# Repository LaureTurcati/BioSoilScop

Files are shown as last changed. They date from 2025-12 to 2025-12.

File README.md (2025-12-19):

# BioSoilScop
The VerY cool Cam Trap for soil ORganisms (VYCTOR)

This camera trap was designed to study ground fauna without disturbing or killing it.

VYCTOR consists of a waterproof sensor measuring approximately 25x25cm with removable and interchangeable 10cm feet. It is capable of taking images day and night thanks to a brightness detection device that activates a night vision mode with 8 infrared LEDs surrounding the camera. The system is controlled by a Raspberry Pi. The camera films continuously at low resolution (without recording) and an algorithm detects movement by comparing images in pairs (background subtraction + speed calculation + shape detection). When movement is detected, a series of high-definition photos is taken at regular intervals and stored. The device is powered by mains electricity or battery. A computer interface allows the measurement settings to be configured and the characteristics of the installation site to be entered. It has been designed to be easy to use by non-specialists.

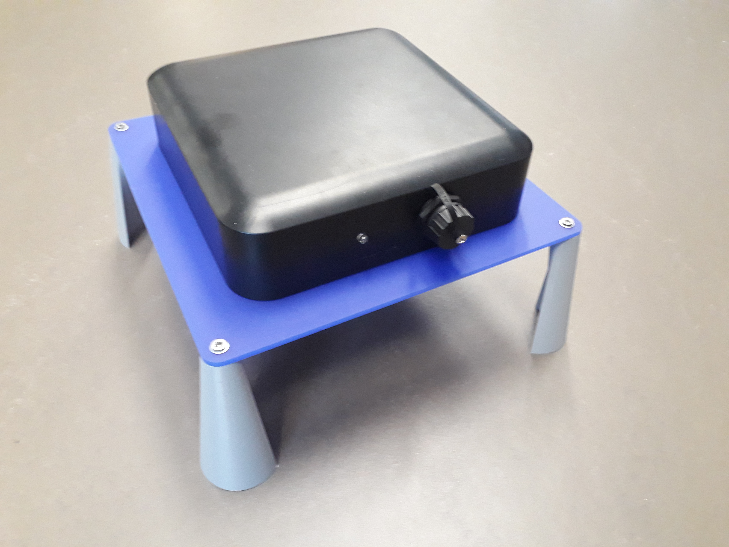
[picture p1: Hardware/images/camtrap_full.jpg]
full

<ins>Picture of the VYCTOR device </ins>  

 ## Examples of pictures taken
Here are some images taken during a laboratory test session.

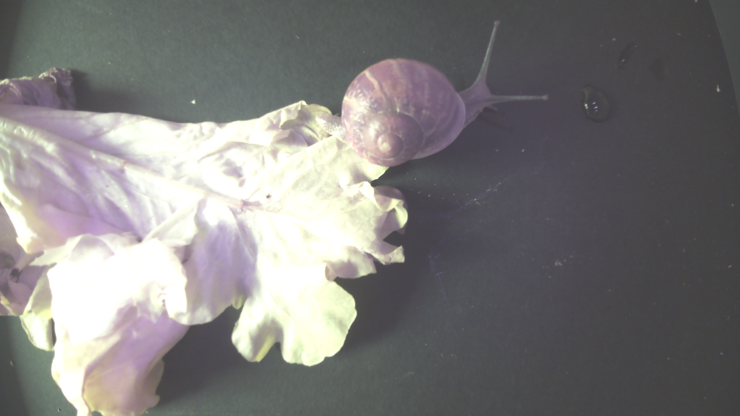
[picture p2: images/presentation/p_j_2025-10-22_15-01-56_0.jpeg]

<ins>Taken picture of a snail after motion detection</ins>

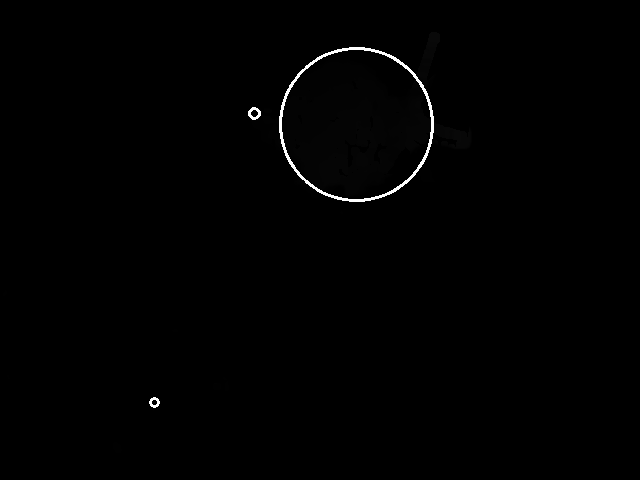
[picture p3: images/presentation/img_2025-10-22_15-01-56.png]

<ins>Motion detection representation</ins>

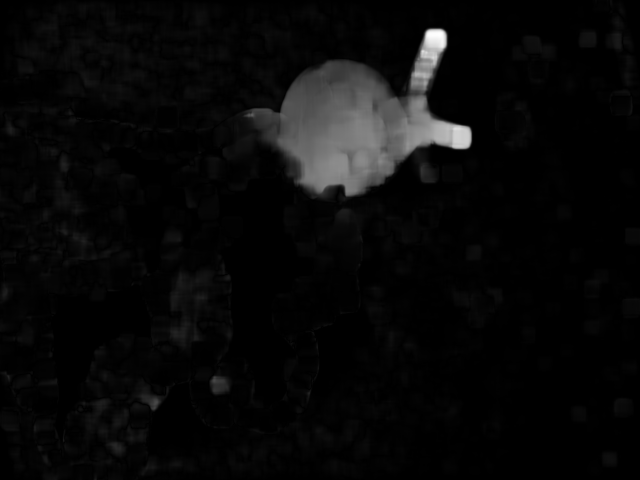
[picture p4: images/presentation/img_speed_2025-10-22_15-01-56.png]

<ins>Speed detection representation</ins>

## Construction
Browse the hardware folder to construct your VYCTOR

## Documentation
Recover the documentation user and developpement in the Folder Software

## Credit
This project was funded by the French national research agency (ANR) BISES ANR-19-CE 32-0012, the OSU OREME and the OSU Ecce Terra

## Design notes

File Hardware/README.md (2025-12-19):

# CamTrap Hardware

Le CamTrap est organisé autour d'un Raspberry Pi.  
Il contient des parties imprimées en 3D et découpé au laser, cependant il est possible de faire sans.

## logiciels utilisés

Les PCBs ont été réalisés avec Kicad 7.0.
Les tracés laser avec Inkscape.

## Liste du Matériel

La liste du matériel se trouve dans le fichier "camtrap_bom.xlsx".

## Schéma de connection

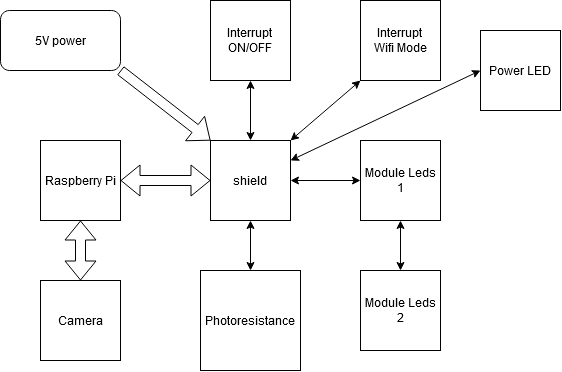
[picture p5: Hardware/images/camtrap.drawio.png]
connections


## Liste des dossiers

Hardware  
├── camtrap/    
├── camtrap_usb_adapteur/  
├── camtrap3d/  
├── images/  
└── camtrap-leds/  

- **`camtrap`** : Contient les fichiers de fabrication de la carte head au dessus du Raspberry.  
- **`camtrap_usb_adapteur`** : Contient les fichiers de fabrication de la petite carte d'adaptation de la prise USB.  
- **`camtrap3d`** : Contient les fichiers d'impression et de découpe.  
- **`images`** : Contient les images pour le readme.  
- **`camtrap-leds`** :  Contient les fichiers de fabrication de la carte qui tient les leds

## Vue globale 

full

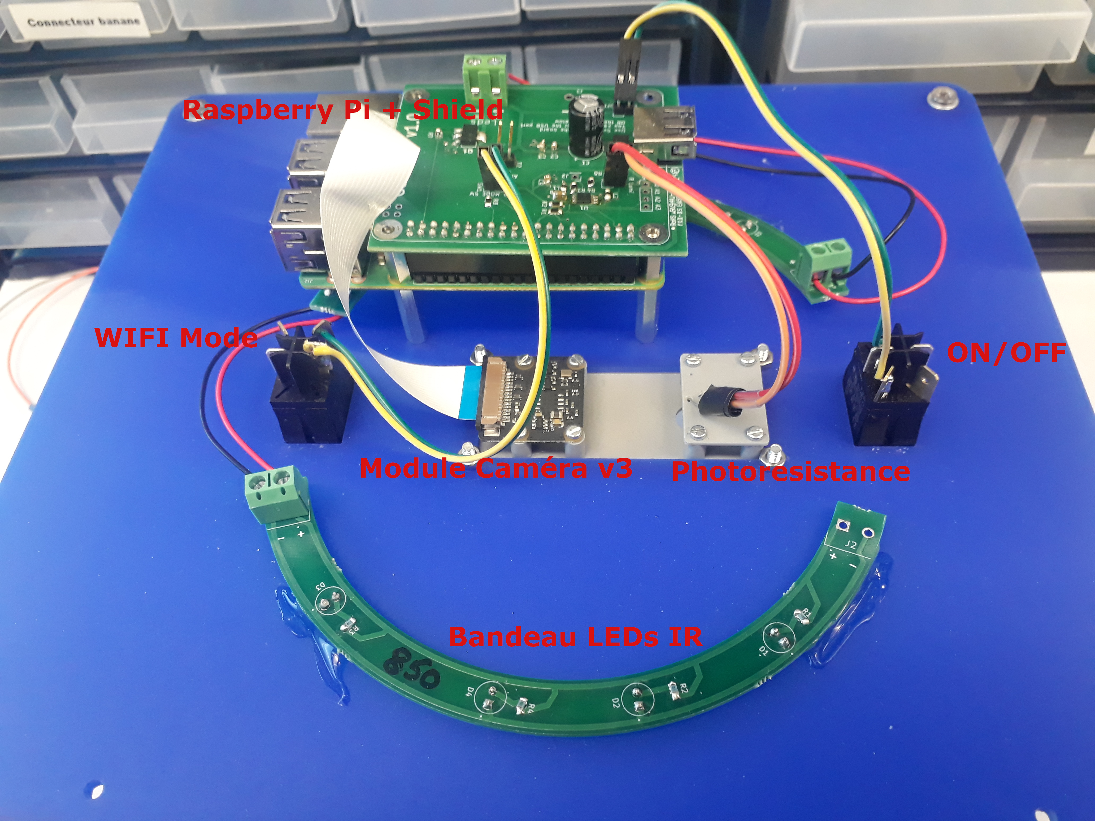
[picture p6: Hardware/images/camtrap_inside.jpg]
inside


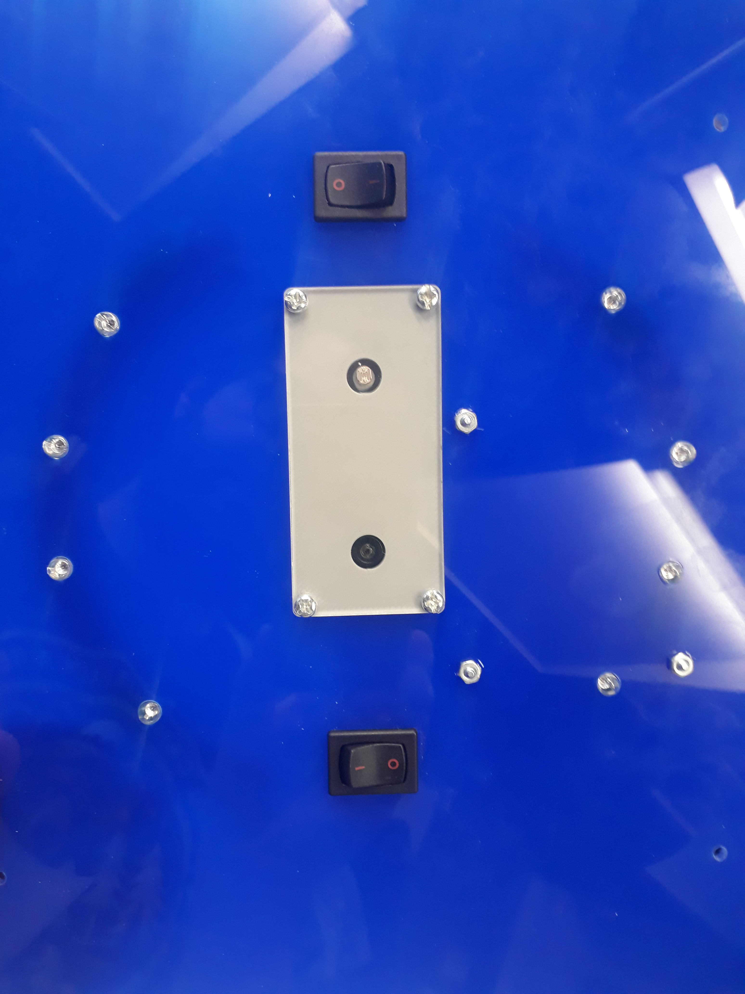
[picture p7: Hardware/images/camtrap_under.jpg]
under


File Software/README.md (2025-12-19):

# CamTrap Software

[Mettre un OS sur le Raspberry pi](./RaspberryPiOS.md)

## Interface

[Documentation développement](./interface/Readme.md)  
[Documentation utilisation](./interface/CamTrap.md)  

## Application

[Documentation](./application/Readme.md)

## Organisation

home/  
├── ADS1115/  
├── app/  
├── interface/  
└── camtrap/  

- **`ADS1115`** : Environnement utile pour l'app
- **`app`** : Application
- **`interface`** : Interface
- **`camtrap`** : Dossier de stockage des config, et des dossiers de sessions.

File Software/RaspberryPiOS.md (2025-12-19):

# Installation d'un OS sur un Raspberry Pi avec Raspberry Pi Imager

Ce guide est un rappel pour installer un OS sur un Raspberry Pi en utilisant **Raspberry Pi Imager** sous Ubuntu.

---

## 1. Installation de Raspberry Pi Imager

### 1.1 Via le Store Ubuntu

1. Ouvrir le **Store Ubuntu**.
2. Rechercher et installer **Raspberry Pi Imager**.

### 1.2 Installation manuelle via fichier .deb

1. Télécharger le fichier `.deb` depuis le site officiel : [Raspberry Pi Imager](https://www.raspberrypi.org/software/).
   - Exemple de fichier : `imager_x.x.x_amd64.deb`
2. Ouvrir un terminal et exécuter les commandes suivantes :

    ```bash
    cd ~/Téléchargements
    sudo apt install ./imager_x.x.x_amd64.deb
    ```

---

## 2. Télécharger et flasher l'OS

### 2.1 Utilisation de Raspberry Pi Imager

1. Ouvrir **Raspberry Pi Imager**.
2. Rechercher et sélectionner l'OS souhaité dans la liste proposée.

### 2.2 Si l'OS n'est pas disponible dans la liste

1. Télécharger l'image `.zip` de l'OS depuis un site officiel.
2. (Optionnel) Vérifier l'intégrité du fichier téléchargé en comparant le **hash SHA256**.

#### Vérification du fichier avec SHA256

- Télécharger également le fichier `.zip.sha256`.
- Calculer le hash du fichier téléchargé :

    ```bash
    sha256sum ./chemin/vers/fichier.zip
    ```

- Comparer le résultat avec le contenu du fichier `.zip.sha256` :

    ```bash
    diff <(sha256sum ./chemin/vers/fichier.zip) fichier.sha256
    ```

Si le hash est correct, vous pouvez continuer.

### 2.3 Flash de l'OS sur la carte SD

1. Insérer la **carte SD** du Raspberry Pi dans le PC.
2. Dans **Raspberry Pi Imager**, choisir **"Use custom"** pour sélectionner l'image téléchargée.
3. Sélectionner la **carte SD** comme destination de l'écriture.
4. Cliquer sur **"Écrire"** pour flasher l'OS.

---

## 3. Préparer le Raspberry Pi

1. Retirer la carte SD du PC et l'insérer dans le Raspberry Pi.
2. Démarrer le Raspberry Pi.

### 3.1 Mettre à jour le Raspberry Pi

1. Mettre à jour la date du système (si nécessaire) :

    ```bash
    sudo date -s 'yyyy-mm-dd hh:mm:ss'
    ```

2. Mettre à jour les paquets du système :

    ```bash
    sudo apt update
    sudo apt upgrade
    ```

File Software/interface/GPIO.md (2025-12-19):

# GPIO

##### Mise en place du bouton 

| Couleur du fil  | PIN | Couleur PIN |
|  :---:  |  :----:  |  :---:  |
| Rouge | 3V3 | Orange |
| Blanc | Ground | Noir |
| Noir | GPIO22 | Vert |
___
##### Rédaction du script permettant de passer le raspberry pi en mode wifi ou en mode ap en fonction de la position du bouton
- wifi_ap_gpio.py :
```python
import RPi.GPIO as GPIO
import time
import subprocess

GPIO.setmode(GPIO.BCM)  
GPIO_PIN = 22 
GPIO.setup(GPIO_PIN, GPIO.IN) 

def switch_mode(mode):
    if mode == 0:
        print("Switching to WiFi mode")
        subprocess.call(['sudo', '/home/pi/bookworm_wifi_ap_switch.sh', 'wifi'])
    elif mode == 1:
        print("Switching to AP mode")
        subprocess.call(['sudo', '/home/pi/bookworm_wifi_ap_switch.sh', 'ap']) 

try:
    mode = GPIO.input(GPIO_PIN)
    switch_mode(mode)
finally:
    GPIO.cleanup()
```
___
##### Modification des droits 
```bash
sudo chmod +x wifi_ap_gpio.py
sudo chmod +x bookworm_wifi_ap_switch.sh
```
___
##### Lancement du script au boot
```bash
sudo nano /etc/rc.local
```
1. /etc/rc.local :
```
python3 /home/pi/wifi_ap_gpio.py &
```
2. reboot
```bash
sudo reboot
```
3. Voir status :
```bash
systemctl status rc-local
```
4. Voir logs : 
```bash
journalctl -u rc-local
```

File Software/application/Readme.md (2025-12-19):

# Application de Capture de Photos

## Table des Matières
1. [Introduction](#introduction)
2. [Prérequis](#prérequis)
3. [Structure du Projet](#structure-du-projet)
4. [Configuration des Environnements](#configuration-des-environnements)
5. [Fonctionnalités](#fonctionnalités)
    - [Démarrage du Programme](#démarrage-du-programme)
    - [Session en Mode "Continue"](#session-en-mode-continue)
    - [Session en Mode "Plage"](#session-en-mode-plage)
    - [Detection des objets mobiles](#detection-des-objets-mobiles)

___
## Introduction

Cette application permet de capturer des photos en fonction de la détection de mouvement et de luminosité. Elle utilise une caméra, un capteur de luminosité (ADS1115), et des fichiers de configuration pour ajuster son comportement.

___
## Prérequis

Pour exécuter l'application, vous devez disposer des éléments suivants :

- **Python 3** installé sur le système CamTrap.
- **SSH** activé sur le CamTrap pour un accès distant.
- L'outil `scp` pour transférer les fichiers si vous développez sur une machine distante.

___
## Structure du Projet

Voici l'organisation des fichiers et dossiers principaux :

home/  
├── ADS1115/  
├── app/  
│&emsp;&emsp;&nbsp;&nbsp;&nbsp;├── [ \_\_init\_\_.py](./__init__.py)  
│&emsp;&emsp;&nbsp;&nbsp;&nbsp;├── [ads_luminosity.py](./ads_luminosity.py)  
│&emsp;&emsp;&nbsp;&nbsp;&nbsp;├── [camera.py](./camera.py)  
│&emsp;&emsp;&nbsp;&nbsp;&nbsp;├── [config.py](./config.py)  
│&emsp;&emsp;&nbsp;&nbsp;&nbsp;├── [image.py](./image.py)  
│&emsp;&emsp;&nbsp;&nbsp;&nbsp;├── [log.py](./log.py)  
│&emsp;&emsp;&nbsp;&nbsp;&nbsp;├── [luminosity.py](./luminosity.py)  
│&emsp;&emsp;&nbsp;&nbsp;&nbsp;├── [motion.py](./motion.py)  
│&emsp;&emsp;&nbsp;&nbsp;&nbsp;├── [script.py](./script.py)  
│&emsp;&emsp;&nbsp;&nbsp;&nbsp;├── [session.py](./session.py)
│&emsp;&emsp;&nbsp;&nbsp;&nbsp;├── [set_video.py](./set_video.py)
└── &emsp;└── [Readme.md](./Readme.md)  

___
## Configuration des Environnements

### Environnement ADS1115
Pour le capteur de luminosité :

```bash
sudo python3 -m venv ads1115
source ads1115/bin/activate
sudo pip3 install adafruit-circuitpython-ads1x15
```

### Environement Global

```bash
sudo apt install libcamera-apps python3-libcamera python3-picamera2
sudo apt install python3-rpi.gpio
sudo apt install python3-opencv opencv-data ffmpeg
sudo apt install -y python3-prctl libatlas-base-dev ffmpeg python3-pip
```

___
## Fonctionnalités

### Sessions
L'application utilise les fichiers de configuration situés dans `home/camtrap/config.json` pour configurer la caméra. Elle dispose de deux modes principaux : **"continue"** et **"plage"**.

#### Démarrage du Programme

##### Récupération des paramètres :

- Charger les paramètres de la session.
- Ajouter un log indiquant le chargement des paramètres.

##### Initialisation des variables :

- Charger les paramètres généraux, de la caméra, et de luminosité.
- Ajouter un log confirmant l'initialisation.

#### Session en Mode "Continue"

##### Initialiser les threads :

- Configurer et démarrer la caméra en mode continu (ajouter un log).
- Démarrer le capteur de luminosité avec l'environnement ADS1115 (ajouter un log).

##### Boucle principale :

- **Vérifier la luminosité :**
  - Si elle est inférieure à `th_jour` : passer en mode nuit (log ajouté).
  - Si elle est supérieure à `th_nuit` : passer en mode jour (log ajouté).
- **Détecter les mouvements :**
  - Si un mouvement est détecté, capturer une photo (log ajouté).

#### Session en Mode "Plage"

##### Initialiser les threads :

- Configurer et démarrer la caméra en mode continu (ajouter un log).
- Démarrer le capteur de luminosité avec l'environnement ADS1115 (ajouter un log).

##### Boucle principale :

- **Vérifier si le jour actuel est dans la plage définie** (`jour_debut` à `jour_fin`) :
  - Si oui, vérifier les créneaux horaires définis dans `time_slots` :
    - Si l'heure actuelle correspond à un créneau, continuer.
    - **Vérifier la luminosité :**
      - Si elle est inférieure à `th_jour` : passer en mode nuit (log ajouté).
      - Si elle est supérieure à `th_nuit` : passer en mode jour (log ajouté).
    - **Détecter les mouvements :**
      - Si un mouvement est détecté, capturer une photo (log ajouté).

#### Detection des objets mobiles
- La prise de photos dans la classe Image est pilotée par la détection d'insectes par une instance de la classe Detector.
- La classe detector permet d'identifier la présence d'objets mobiles dans le champ, de les distinguer d'un "background" et d'en mesurer la taille et la vitesse.
    - Identification du background 
        - L'intérêt est de séparer les mouvements d'insectes des changements de luminosité ou autres mouvements parasites (ex : brins d'herbe qui bougent)
        - Mise à jour du background avec un algorithme de soustraction de fond (BackgroundSubtractorMOG2 de OpenCV)
        - Le background est mis à jour pendant un certain nombre d'images (paramétrable) avant d'être considéré comme stable.
        - Le background est réinitialisé régulièrement, notamment après chaque prise de photos afin de s'adapter aux changements de luminosité.
    - Détection de présente d'objets mobiles
        - Retrait du background de l'image courante
        - Calcul de vitesse en comparant deux images successives
        - Identification des objets mobiles par détection de contours ou de blobs
            - Détection de contours : identifications de gradients (Canny) + fermeture morphologique (identifications de "bords contigus") + approximation de polygone + calcul d'aire 
            - Détection de blobs : SimpleBlobDetector (OpenCV) + calculd'aire
        - Filtrage des objets selon leur taille et leur vitesse 
- Deux threads distincts sont utilisés pour mettre à jour le background en permalence et effectuer la détection à intervalles réguliers.  
- Paramètres ajustables :
    - Vitesse minimale et maximale à considérer : min_shape_speed, max_shape_speed (px/sec)
    - Taille minimale et maximale à considérer : min_shape_area, max_shape_area (px^2)
    - Background :
        - Nombre d'images avant que le fond soit considéré comme stable : pictures_before_bg_is_set
        - Taille de l'historique pour le modèle de fond : history 
    - Méthode de détection : contours ou blobs (blobs semble bien mieux fonctionner)
        - Blobs : 
            - flou : blur_kernel (~5)
            - inertie de la forme (allongée/circulaire) : minInertiaRatio (~0.1), maxInertiaRatio (~1) 
        - Contours : 
            - flou : blur_kernel (~9)
            - Canny : canny_threshold_1 (~14), canny_threshold_2 (~36)
            - Fermeture morphologique : closing_kernel (~5), closing_iterations (~1)

### Capture Vidéo

``` bash
ffplay -f rawvideo -pixel_format yuv420p -video_size 1536x864 <nom_video>
ffplay -f rawvideo -pixel_format yuv420p -video_size 640x480 <nom_video>
```

#### Paramètres disponibles
- **Qualité vidéo** : Choix entre **Low** et **High**.
- **Intensité des LEDs** : Ajustez l'intensité des LEDs selon vos préférences.
- **Durée de la vidéo** : La durée maximale de la vidéo est de **60 secondes**.

De plus, la caméra ce paramètre en utilisant le fichier de config `/home/pi/camtrap/config.json`

##### Fichier vidéo généré
En fonction du choix de la qualité vidéo, la caméra génère un fichier `.raw`, qui est un fichier vidéo brut. Le format du fichier dépend des critères suivants :
- Taille (size)
- Format
- Encodeur (généralement `null`)

#### Pré-requis

Avant de commencer, assurez-vous que **ffplay** est installé sur votre machine.

- Version requise : `5.1.6` ou supérieure.

#### Lecture du fichier `.raw`

Une fois la vidéo capturée, vous pouvez la lire avec **ffplay** en utilisant les commandes suivantes, adaptées à la qualité choisie :

- Pour une vidéo en qualité **High** (1536x864) :
  ```bash
  ffplay -f rawvideo -pixel_format yuv420p -video_size 1536x864 <nom_video>
  ```
- Pour une vidéo de qualité **Low** (640x864) :
  ```bash
  ffplay -f rawvideo -pixel_format yuv420p -video_size 640x480 <nom_video>
  ```

___
## Paramètre de la caméra

Voir les [paramètres](./Parametres.md).

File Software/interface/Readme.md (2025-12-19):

# Interface pour Communiquer avec un CamTrap (Bookworm)

 <!-- introduire CamTrap 
___ -->
## Table des Matières
- [Interface pour Communiquer avec un CamTrap (Bookworm)](#interface-pour-communiquer-avec-un-camtrap-bookworm)
  - [Table des Matières](#table-des-matières)
  - [Introduction](#introduction)
  - [Prérequis](#prérequis)
  - [Installation](#installation)
      - [Étape 1 : Installation de Flask](#étape-1--installation-de-flask)
      - [Étape 2 : Construire l'Arborescence de Fichiers](#étape-2--construire-larborescence-de-fichiers)
      - [Étape 3 : Déploiement de l'Interface](#étape-3--déploiement-de-linterface)
  - [Détails Techniques](#détails-techniques)
      - [Fonctionnement de `server.py` et des Pages HTML](#fonctionnement-de-serverpy-et-des-pages-html)
      - [Utilisation du Map Picker (en mode WiFi)](#utilisation-du-map-picker-en-mode-wifi)
  - [Utilisation](#utilisation)
    - [Mode de Fonctionnement du CamTrap](#mode-de-fonctionnement-du-camtrap)
    - [Navigation de Fichiers avec FileBrowser](#navigation-de-fichiers-avec-filebrowser)
        - [Modification des droits](#modification-des-droits)
  - [Configuration de la mise en route du serveur et du script pour les boutons au démarage du CamTrap](#configuration-de-la-mise-en-route-du-serveur-et-du-script-pour-les-boutons-au-démarage-du-camtrap)
  - [Erreur corrigé](#erreur-corrigé)
          - [Remarques :](#remarques-)
___
## Introduction

Cette interface permet aux utilisateurs de se connecter à leur CamTrap (ayant un OS "bookworm") via leur réseau, en utilisant une interface web accessible depuis l'adresse suivante : [`http://raspberrypi.local:5000`](http://raspberrypi.local:5000) ou via l'adresse IP locale de votre CamTrap. L'accessibilité via le lien est possible grâce à l'outil `avahi-daemon`, qui est généralement activé par défaut.
___
## Prérequis

- Un CamTrap (ayant un OS bookworm).
- Python 3 installé sur le CamTrap.
- SSH activé sur le CamTrap.
- `scp` pour transférer les fichiers si l'interface est développée sur une machine distante.
- GPIO activé sur le Rasberry Pi.
___
## Installation

#### Étape 1 : Installation de Flask

Pour que l'interface fonctionne, Flask doit être installé sur votre CamTrap. Voici les étapes pour vérifier et installer Flask :

1. **Vérification de Flask**

    Pour vérifier si Flask est déjà installé, exécutez la commande suivante :

    ```bash
    python3 -m pip show flask
    ```

2. **Installation de `pip`**

    Si `pip` n'est pas déjà installé, installez-le avec les commandes suivantes :

    ```bash
    sudo apt update
    sudo apt install python3-pip
    sudo apt install python3-dotenv
    ```

3. **Installation de Flask**

    Ensuite, installez Flask :

    ```bash
    python3 -m pip install Flask
    ```

#### Étape 2 : Construire l'Arborescence de Fichiers

Voici l'arborescence des fichiers nécessaire pour le projet :

interface/  
├── static/  
│&emsp;&emsp;├── css/  
│&emsp;&emsp;&emsp;&emsp;└── [style.css](./static/css/style.css)  
│&emsp;&emsp;├── img/  
│&emsp;&emsp;└──  js/  
│&emsp;&emsp;&emsp;&emsp;├──[map_picker.js](./static/js/map_picker.js)  
│&emsp;&emsp;&emsp;&emsp;└── [script.js](./static/js/script.js)  
├── templates/  
│&emsp;&emsp;├── [ap_mode.html](./templates/ap_mode.html)  
│&emsp;&emsp;├── [config_app.html](./templates/config_app.html)  
│&emsp;&emsp;├── [date.html](./templates/date.html)  
│&emsp;&emsp;├── [espace_disk.html](./templates/espace_disk.html)  
│&emsp;&emsp;├── [filebrowser.html](./templates/filebrowser.html)  
│&emsp;&emsp;├── [index.html](./templates/index.html)  
│&emsp;&emsp;├── [liste_session.html](./templates/liste_session.html)  
│&emsp;&emsp;├── [new_session.html](./templates/new_session.html)  
│&emsp;&emsp;└── [wifi_mode.html](./templates/wifi_mode.html)  
├── [Readme.md](./Readme.md)  
└── [server.py](./server.py)    

- **`static/`** : Contient les images, les fichiers CSS et JavaScript.
- **`templates/`** : Contient les fichiers HTML qui seront rendus par Flask.
- **`server.py`** : Le script Python qui lance le serveur Flask.
- **`Readme.md`** : Cette documentation.

#### Étape 3 : Déploiement de l'Interface

Pour déployer l'interface, suivez ces étapes :

1. **Transfert des fichiers vers le CamTrap**

    Si vous avez développé l'interface sur une autre machine, transférez le dossier `interface/` vers le CamTrap en utilisant la commande `scp` :

    ```bash
    scp -r Documents/raspberrypi/bookworm/interface/ pi@192.168.0.104:/home/pi/Documents
    ```

2. **Lancer le serveur Flask**

    Connectez-vous au CamTrap, puis démarrez le serveur Flask en exécutant le fichier `server.py` :

    ```bash
    python3  Documents/interface/server.py
    ```

    Par défaut, l'interface sera accessible via l'adresse `http://raspberrypi.local:5000`.
___
## Détails Techniques

#### Fonctionnement de `server.py` et des Pages HTML

Le fichier **`server.py`** gère les routes et les interactions entre l’utilisateur et les pages HTML via le serveur Flask.

- **Routes Flask** : Chaque page de l'interface est reliée à une route spécifique dans `server.py`, accessible par des requêtes `GET` ou `POST` en fonction des besoins :
  - Les requêtes **`GET`** permettent d’afficher les pages, comme la page d’accueil (`index.html`).
  - Les requêtes **`POST`** sont utilisées pour envoyer des données, par exemple lors de la création de nouvelles sessions ou de configurations réseau.

- **Templates HTML** : Les fichiers HTML dans le dossier `templates/` sont rendus par Flask à l'aide de la fonction `render_template`, permettant une séparation claire entre le code Python et le contenu HTML.

#### Utilisation du Map Picker (en mode WiFi)

L'interface utilise un **Map Picker** pour la sélection de localisation, implémenté avec **Leaflet.js**, une bibliothèque JavaScript populaire pour des cartes interactives.

- **Fonctionnalités** : Les utilisateurs peuvent cliquer sur une carte pour sélectionner des coordonnées géographiques, qui sont ensuite envoyées au serveur pour traitement.
- **Documentation Leaflet** : Pour plus d’informations sur la personnalisation et les fonctionnalités de Leaflet.js, consultez la [documentation officielle](https://leafletjs.com/).
___

## Utilisation

1. Assurez-vous que le CamTrap est connecté au même réseau que votre ordinateur.
2. Ouvrez un navigateur web et accédez à l'URL suivante : [`http://raspberrypi.local:5000`](http://raspberrypi.local:5000).
3. Utilisez les fonctionnalités proposées pour interagir avec le CamTrap, comme la navigation de fichiers ou la configuration réseau.

### Mode de Fonctionnement du CamTrap

Le CamTrap est équipé d'un bouton permettant de sélectionner le mode de fonctionnement (Voir la [Documentation](GPIO.md)):

- **Mode Wi-Fi (0)** : Si le bouton est positionné sur **0**, le CamTrap démarre en mode Wi-Fi standard, se connectant à votre réseau sans fil configuré.
- **Mode AP (1)** : Si le bouton est positionné sur **1**, le CamTrap démarre en mode Point d'Accès (AP), permettant aux autres appareils de se connecter directement au CamTrap.git p

Assurez-vous de régler le bouton selon vos besoins avant de démarrer le CamTrap pour utiliser l'interface web appropriée.

### Navigation de Fichiers avec FileBrowser

Le CamTrap permet également de naviguer et de gérer les fichiers directement via une interface web : 

- Visualisation des fichiers et dossiers présents sur le CamTrap.
- Téléchargement et gestion des fichiers via l'interface.
- Accès à des fonctionnalités de recherche et de tri pour faciliter l'utilisation.

Pour l'installation (Voir la [Docummentation](filebrowser.md)).
___

##### Modification des droits 
```bash
sudo chmod +x interface/server.py
```

___

## Configuration de la mise en route du serveur et du script pour les boutons au démarage du CamTrap
```bash
sudo nano /etc/rc.local
```
1. /etc/rc.local :
```
python3 /home/pi/wifi_ap_gpio.py &

python3 /home/pi/Documents/interface/server.py &
```
> :warning: **Rappel :**  Le contenu de [wifi_ap_gpio.py](GPIO.md#rédaction-du-script-permettant-de-passer-le-raspberry-pi-en-mode-wifi-ou-en-mode-ap-en-fonction-de-la-position-du-bouton)
2. reboot
```bash
sudo reboot
```
3. Voir status :
```bash
systemctl status rc-local
```
4. Voir logs : 
```bash
journalctl -u rc-local
```
commandes disponnibles: 
- aller à la fin du fichier : maj+g
- fermer : q

## Erreur corrigé

###### Remarques :

Au démarrages les pins ne sont pas configurées, ce qui explique pourquoi les LED sont allumées par défaut. Lorsqu'une session est lancée, les pins se configurent correctement. Ainsi, si la session est arrêtée, les LED s'éteignent automatiquement.

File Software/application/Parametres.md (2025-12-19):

# **Guide des paramètres pour la PiCam 3**

Ce document fournit une explication détaillée des paramètres utilisés pour CamTrap via Python et la bibliothèque `picamera2`. Vous trouverez ici des descriptions, des plages de valeurs, et des exemples pratiques pour optimiser vos réglages.

___
## **1. Paramètres généraux**

### `AnalogueGain` (Gain analogique)
- **Description** : Contrôle la sensibilité du capteur à la lumière.
- **Plage de valeurs** : `1.0` (par défaut) à `16.0`.
- **Notes** : 
  - Un gain élevé améliore la luminosité en basse lumière, mais introduit du bruit.

___
### `HdrMode` (Mode HDR)
- **Description** : Active ou ajuste le HDR (High Dynamic Range) pour capturer des détails dans les ombres et les hautes lumières.
- **Modes disponibles** :
  - `0` : Désactivé (par défaut).
  - `1` : Faible HDR.
  - `2` : HDR moyen.
  - `3` : HDR élevé.
  - `4` : Automatique.

___
### `Brightness` (Luminosité)
- **Description** : Ajuste la luminosité globale de l'image.
- **Plage de valeurs** : `-1.0` (minimum) à `1.0` (maximum), `0.0` par défaut.

___
### `Contrast` (Contraste)
- **Description** : Modifie la différence entre les zones sombres et lumineuses.
- **Plage de valeurs** : `0.0` (faible) à `32.0` (élevé), `1.0` par défaut.

___
### `Saturation` (Saturation des couleurs)
- **Description** : Ajuste l'intensité des couleurs dans l'image.
- **Plage de valeurs** : `0.0` (niveaux de gris) à `32.0` (très saturé), `1.0` par défaut.

___
### `Sharpness` (Netteté)
- **Description** : Ajuste la netteté de l'image.
- **Plage de valeurs** : `0.0` (aucune netteté) à `16.0` (très net), `1.0` par défaut.

___
## **2. Paramètres de mise au point**

### `AfMode` (Mode autofocus)
- **Description** : Définit le mode de mise au point automatique.
- **Modes disponibles** :
  - `0` : Auto (par défaut).
  - `1` : Continuous (mise au point continue).

___
### `AfRange` (Plage de mise au point)
- **Description** : Limite la plage de distances pour la mise au point.
- **Modes disponibles** :
  - `0` : Normal (standard).
  - `1` : Macro (proche).
  - `2` : Full (complète).

___
### `AfSpeed` (Vitesse de mise au point)
- **Description** : Contrôle la rapidité de la mise au point.
- **Modes disponibles** :
  - `0` : Normal (équilibré).
  - `1` : Rapide (moins précis).

___
## **3. Paramètre avancé**

### `AeExposureMode` (Mode d'exposition automatique)
- **Description** : Gère automatiquement l'exposition selon la scène.
- **Modes disponibles** :
  - `0` : Auto (par défaut).
  - `1` : Night (faible lumière).
  - `2` : Backlight (contre-jour).
  - `3` : Spotlight (projecteurs).

___
## **4. Exemple d'utilisation avec Python**

```python
from picamera2 import Picamera2
from libcamera import controls

# Initialisation de la caméra
picam2 = Picamera2()
config = picam2.create_preview_configuration()
picam2.configure(config)

# Réglages des paramètres
picam2.set_controls({
    "AnalogueGain": 2.0,
    "AeExposureMode": 0,
    "HdrMode": 3,  # HDR élevé
    "Brightness": 0.5,
    "Contrast": 1.5,
    "Saturation": 1.2,
    "AfMode": 1,  # Autofocus continu
    "AfSpeed": 0,  # Vitesse normale
})

# Démarrage de la capture
picam2.start_preview()
picam2.start()

# Capture d'une image
picam2.capture_file("image.jpg")

# Arrêt de la caméra
picam2.stop()

```

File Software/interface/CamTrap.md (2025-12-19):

# CampTrap

> **Introduction :** CampTrap est une solution permettant de gérer un Raspberry Pi configuré en différents modes pour des utilisations spécifiques.

## Table des matières
1. [Introduction](#introduction)
2. [Quick start](#quick-start)
3. [CamTrap](#raspberry-pi)
    - [Étape 1 : Démarrage du CamTrap](#étape-1--démarrage-du-raspberry-pi)
    - [Étape 2 : Lancement de l'interface](#étape-2--lancement-de-linterface)
4. [Page d'accueil](#page-daccueil)
5. [Mode de Connexion](#mode-de-connexion)
6. [Configuration de l'Application](#configuration-de-lapplication)
7. [Configuration de la Date](#configuration-de-la-date)
8. [Filebrowser](#comment-avoir-accès-au-photos-)
9. [Conclusion](#conclusion)

___
## Introduction
**L'interface** est conçu pour faciliter l'utilisation et la configuration de votre CamTrap.
___
## Quick Start

### Étape 1 : Préparation

1. **Positionnez le bouton de mode de fonctionnement** sur :
   - **0** pour le mode Wi-Fi
   - **1** pour le mode Point d'Accès (AP)
   > Pour le premier démarrage, mettez le bouton sur **1** (mode AP).

### Étape 2 : Connexion au Raspberry Pi
1. **Allumez le Raspberry Pi** en vérifiant que le bouton est bien positionné.
2. **Connectez votre ordinateur** au bon Wi-Fi.

### Étape 3 : Accéder à l'interface web
1. **Ouvrez un navigateur web** sur votre ordinateur.
2. **Accédez à l'URL** suivante : [`http://raspberrypi.local:5000`](http://raspberrypi.local:5000).

### Étape 4 : Configuration initiale
1. **Configurez la date** via l'onglet **Configuration de la Date** pour garantir le bon fonctionnement.
2. **Accédez à l'onglet "Mode de Connexion"** pour choisir et configurer votre réseau Wi-Fi.
3. **Configuration de l'app** 
4. **Acceder au dossiers photo** en démarant le service permettant d'avoir accès au 'drive' des documents et l'ouvrir via l'onglet Filebrowser.

___
## CamTrap

### Étape 1 : Démarrage du CamTrap
Votre CamTrap est équipé d'un bouton permettant de sélectionner le mode de fonctionnement :

- **Mode Wi-Fi (0)** : Si le bouton est positionné sur **0**, le CamTrap démarre en mode Wi-Fi standard, se connectant à votre réseau sans fil configuré.
- **Mode AP (1)** : Si le bouton est positionné sur **1**, le CamTrap démarre en mode Point d'Accès (AP), permettant aux autres appareils de se connecter directement au CamTrap.

> :warning: **Attention :** Pour le premier démarrage, choisissez le mode **AP** car le Wi-Fi n'est pas encore configuré.

Assurez-vous de régler le bouton selon vos besoins avant de démarrer le CamTrap pour utiliser l'interface web.

### Étape 2 : Lancement de l'interface
1. Assurez-vous que le CamTrap est connecté au même réseau que votre ordinateur.
2. Ouvrez un navigateur web et accédez à l'URL suivante : [`http://raspberrypi.local:5000`](http://raspberrypi.local:5000).

___

## Page d'accueil

Contient des informations sur le projet.
___
## Mode de Connexion

#### Mode Wi-FI
- Permet de passer le CamTrap en mode **Wi-Fi** en utilisant le bouton.

#### Mode AP
- Affichage des réseaux déjà associés
- Passage en mode **Wi-Fi**
- Ajout d'un réseau Wi-Fi (ce qui connecte le CamTrap au nouveau réseau Wi-Fi associé)
___
## Configuration de l'Application
L'onglet **Configuration de l'Application** permet de modifier les paramètres de la caméra. Voici les différents paramètres configurables :

- **Gain** : Permet de régler le niveau de gain pour ajuster la sensibilité de la caméra à la lumière, utile dans des environnements à faible luminosité.
*Valeur par défaut : 0*
- **Exposure** : Contrôle l'exposition pour équilibrer la luminosité de l'image, en ajustant la durée pendant laquelle la caméra capture la lumière.
*Valeur par défaut : normal*
- **HDR** : Active ou désactive le mode High Dynamic Range (HDR) pour capturer une plage plus large de luminosité, permettant de mieux gérer les scènes avec des contrastes élevés.
*Valeur par défaut : off*
- **Brightness** : Ajuste la luminosité générale de l'image, influençant la clarté de la scène.
*Valeur par défaut : 0*
- **Contrast** : Modifie le contraste entre les parties sombres et claires de l'image pour ajouter de la profondeur et du détail.
*Valeur par défaut : 1*
- **Saturation** : Contrôle l'intensité des couleurs dans l'image, utile pour obtenir des couleurs vives ou plus naturelles.
*Valeur par défaut : 1*
- **Autofocus Mode** : Sélectionne le mode de mise au point automatique, comme le mode continu ou ponctuel, en fonction de la nature des sujets à capturer.
*Valeur par défaut : default*
- **Autofocus Range** : Définit la plage de distance sur laquelle l'autofocus doit fonctionner, comme le mode proche ou éloigné, selon les besoins de la prise de vue.
*Valeur par défaut : normal*
- **Autofocus Speed** : Ajuste la vitesse de l'autofocus, pour une mise au point rapide ou plus lente, adaptée aux sujets statiques ou en mouvement.
*Valeur par défaut : normal*

___
## Configuration de la Date 
L'onglet **Configuration de la Date** permet de vérifier et de mettre à jour la date et l'heure du CamTrap.

- **Affichage de la date actuelle** : La date et l'heure actuelles du CamTrap sont affichées.
- **Mise à jour de la Date** : Lors de l'utilisation du CamTrap après une longue période d'inactivité, il est important de vérifier et de mettre à jour la date pour assurer le bon fonctionnement des services réseau et des certificats.

#### Comment mettre à jour la date :
1. Rendez-vous sur l'onglet **Configuration de la Date**.
2. Vérifiez la date affichée.
3. Utilisez le formulaire pour entrer la date correcte si nécessaire.
___
## Sessions

#### Nouvelle session
L'onglet **Création de session** offre un formulaire pour définir une nouvelle session de prise de vue. Vous pouvez choisir de configurer la session :
- **En continu** : pour une capture de photos sans interruption.
- **Sur une plage horaire** : en spécifiant des créneaux horaires ainsi que des dates de début et de fin.

De plus, il est possible d’associer plusieurs informations à chaque session, telles qu’une description et la position géographique du CamTrap.

#### Liste des sessions
L'onglet **Liste des sessions** permet d'afficher un tableau des différentes sessions existantes. À partir de cet onglet, vous pouvez :
- **Démarrer une session** : lancé la capture de photos pour une nouvelle session.
- **Stopper une session** : arrêter la capture de photos en cours.
- **Supprimer une session** : retirer une session qui n'est plus nécessaire.
___
## Comment avoir accès au photos ?
L'onglet Filebrowser va nous permettre de démarrer un service nous permettant d'avoir accès aux dossiers photos.
1. Démarrage du service Filebrowser
2. Ouverture dans un autre onglet du 'drive'
3. Identifiant : admin | Password : admin
___

## Conclusion
Ce guide vise à vous aider à démarrer et à utiliser **L'interface** de manière optimale.

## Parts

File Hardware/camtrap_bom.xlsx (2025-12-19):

 | CamTrap BOM
 | total | 284.38 €
 | pièce | quantité | prix unitaire HT | total HT | lien | Colonne1
 | raspberry pi 3 b+ | 1 | 33.55 | 33.55 | https://www.mouser.fr/ProductDetail/Raspberry-Pi/SC0073?qs=T%252BzbugeAwjiaAHAA%2F5Vfqw%3D%3D
 | carte mémoire sd 64 Go | 1 | 11.42 | 11.42 | https://www.mouser.fr/ProductDetail/Kingston/SDCS2-64GBCA?qs=HFfMDpzxxd1VtEC8LIlGIg%3D%3D
 | Camera Module 3 Wide NoIR | 1 | 32.55 | 32.55 | https://www.mouser.fr/ProductDetail/Raspberry-Pi/SC0875?qs=rQFj71Wb1eXfj0QIwylxWA%3D%3D
 | cable cam 20 cm | 1 | 1.81 | 1.81 | https://www.mouser.fr/ProductDetail/Adafruit/1647?qs=GURawfaeGuCW4KvAYeV3HA%3D%3D
 | embase raspi | 1 | 1.82 | 1.82 | https://www.mouser.fr/ProductDetail/Wurth-Elektronik/61304021821?qs=bZr6mbWTK5mzEvTTGhcEyQ%3D%3D
 | interrupteur | 2 | 2.25 | 4.5 | https://www.mouser.fr/ProductDetail/Carling-Technologies/62115919-0-9-V?qs=5ruQBStH4q%252BWcJ7h%252BdaK5g%3D%3D
 | connecteur usb ext | 1 | 7.31 | 7.31 | https://www.mouser.fr/ProductDetail/Amphenol-LTW/UA-20PMFP-SC8001?qs=BoMHE3Ae0lIld8j0pv3esA%3D%3D
 | capuchon usb | 1 | 2.35 | 2.35 | https://www.mouser.fr/ProductDetail/Amphenol-LTW/CAP-WACMSPC1?qs=BoMHE3Ae0lKpEj6M%252B9qeqg%3D%3D
 | boitier | 1 | 18.51 | 18.51 | https://www.mouser.fr/ProductDetail/Hammond-Manufacturing/1556HABK?qs=9vOqFld9vZVfzVecj7IRHA%3D%3D
 | résistance 0805 500ohms | 1 | 0.15 | 0.15 | https://www.mouser.fr/ProductDetail/ROHM-Semiconductor/KTR10EZPJ511
 | résistance 0805 10 Mohms | 1 | 0.19 | 0.19 | https://www.mouser.fr/ProductDetail/Vishay-Dale/RCC080510M0FKEA?qs=GedFDFLaBXHfedqBQ1aJCw%3D%3D
 | résistance 0805 220ohms | 1 | 0.2 | 0.2 | https://www.mouser.fr/ProductDetail/Panasonic/ERJ-P06F2200V?qs=sGAEpiMZZMtlubZbdhIBIK7FbVYKWV6WTePHHp8Hhqc%3D
 | résistance 0805 10kohms | 5 | 0.13 | 0.65 | https://www.mouser.fr/ProductDetail/Vishay-Dale/RCC080510K0FKEA?qs=GedFDFLaBXGY93oge9hajw%3D%3D
 | résistance 0805 LEDS (270) | 8 | 0.2 | 1.6 | https://www.mouser.fr/ProductDetail/KOA-Speer/RK73H2ARTTD2700F?qs=x6vGwhDZZUZfxlwKGsDIrQ%3D%3D
 | barette male sequable 20p | 1 | 0.8 | 0.8 | https://www.mouser.fr/ProductDetail/Molex/22-28-4205?qs=GAPJcf4kvdu9BJmr7VZajQ%3D%3D
 | barette female sequable 20p | 1 | 2.65 | 2.65 | https://www.mouser.fr/ProductDetail/3M-Electronic-Solutions-Division/929850-01-20-RB?qs=URHRBhDURP%252B6wJ%252Bfq%252BX6nw%3D%3D
 | Photo resistance | 1 | 1.73 | 1.73 | https://www.mouser.fr/ProductDetail/Advanced-Photonix/PDV-P9002?qs=Znm5pLBrcAKw1XlQvWclLA%3D%3D
 | condensateur 0805 1uF | 2 | 0.78 | 1.56 | https://www.mouser.fr/ProductDetail/KYOCERA-AVX/KAF21KR71E105KU?qs=Jm2GQyTW%2FbhAALIO%2FNIvrg%3D%3D
 | condensateur 0805 1nF | 1 | 0.24 | 0.24 | https://www.mouser.fr/ProductDetail/KYOCERA-AVX/KAM21BR72A102KT?qs=OcgtsXO%252B3gszwOFfUTiZ5g%3D%3D
 | condensateur 0805 100nF | 1 | 0.37 | 0.37 | https://www.mouser.fr/ProductDetail/KYOCERA-AVX/KAF21KR72A104KL?qs=Jm2GQyTW%2FbiUCISqVwD%2FLA%3D%3D
 | condensateur chimique radial 220uF | 1 | 0.2 | 0.2 | https://www.mouser.fr/ProductDetail/Lelon/RGA221M1EBK-0811G
 | perles de ferrite | 2 | 0.1 | 0.2 | https://www.mouser.fr/ProductDetail/TDK/MMZ2012Y152BT000?qs=8Kz9Wu9QwqVvXiEqkHUJng%3D%3D
 | convertisseur analogique/ numérique | 1 | 5.77 | 5.77 | https://www.mouser.fr/ProductDetail/Texas-Instruments/ADS1115BQDGSRQ1?qs=34RfhUjJmKdvyLrkbnfjHA%3D%3D
 | transistor / mosfet | 1 | 0.59 | 0.59 | https://www.mouser.fr/ProductDetail/Diodes-Incorporated/FZT851TA?qs=GBLSl2AkiruTgIwj6EDEdg%3D%3D (stock Summit)
 | LED couleur 5mm | 1 | 0.7 | 0.7 | https://www.mouser.fr/ProductDetail/VCC/LTH5MM12VFR4700?qs=Mv7BduZupUimo5j%2F%2F8f9GQ%3D%3D
 | LED IR | 8 | 1.31 | 10.48 | https://www.mouser.fr/ProductDetail/Vishay-Semiconductors/TSHG6400?qs=%2Fjqivxn91cceX9ZJxmpVCg%3D%3D
 | Diodes de protection ESD | 1 | 0.316 | 0.316 | https://www.mouser.fr/ProductDetail/Bourns/SMBJ5.0CA-QH?qs=T94vaHKWudQPoV6jAiwvcA%3D%3D
 | connecteur usb | 1 | 0.865 | 0.865 | https://www.mouser.fr/ProductDetail/Amphenol-FCI/87520-3010ALF?qs=7JiUwvV4mh74F4buwfJ9pg%3D%3D
 | bornier a vis 2 fils | 6 | 0.99 | 5.94 | https://www.mouser.fr/ProductDetail/Phoenix-Contact/1548128?qs=ulEaXIWI0c87QOzP9yohxA%3D%3D
 | PCB led | 2 | 20 | 40
 | PCB main | 1 | 40 | 40
option | PCB adapteur usb | 1 | 0 | 0
 | pied base | 4 | 2 | 8 | impression 3d
 | support cam | 1 | 1 | 1 | impression 3d
 | support photo resistance | 1 | 1 | 1 | impression 3d
 | base plexi | 1 | 20 | 20 | achat + decoupe laser
 | protection lentille | 1 | 5 | 5 | achat + decoupe laser
 | vis m2 6mm | 8 | 0 | 0
 | vis m3 10mm + ecrou | 4 | 0 | 0
 | vis m4 10mm | 4 | 0 | 0
 | standoffs m2,5x11 | 4 | 0.9 | 3.6 | https://www.mouser.fr/ProductDetail/Wurth-Elektronik/971110154?qs=%252BEew9%252B0nqrBAT23nBefr%252Bg%3D%3D
 | standoffs m2,5x20 | 4 | 0.63 | 2.52 | https://www.mouser.fr/ProductDetail/Wurth-Elektronik/971200151?qs=wr8lucFkNMVDo43Tg45BvQ%3D%3D
 | vis m2,5x6 | 8 | 0 | 0
option | batterie 5v | 1 | 64 | 64 | https://fr.rs-online.com/web/p/batteries-externes/2309827?gb=s
option | cable ext usb dupont | 1 | 0 | 0 | https://fr.rs-online.com/web/p/cables-usb/8418743 | ?
 |  |  |  | 0 | https://fr.aliexpress.com/item/1005004266229641.html?src=google

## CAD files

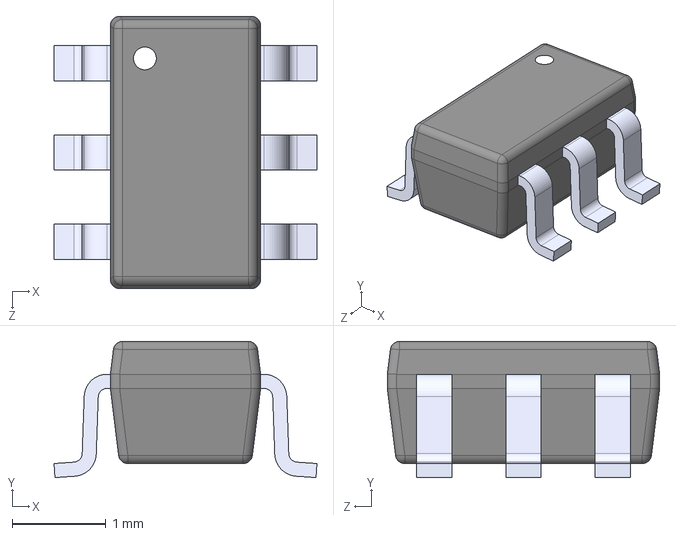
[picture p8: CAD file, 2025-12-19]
Hardware/camtrap/3d/TPS22918DBVR.step
2.80 x 1.45 x 2.90 mm

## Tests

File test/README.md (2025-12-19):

# README

### Overview
This repository contains the implementation and evaluation of algorithms for detecting insects using a Raspberry Pi equipped with a camera. The project aims at improving detection accuracy while maintaining computational efficiency, making it suitable for embedded systems. The algorithms leverage OpenCV functionalities and YOLO-based deep learning models.

### Installation
* Clone the repository
2. Set up a Python virtual environment:
    ```bash
    python3 -m venv detection-algo-env
    source detection-algo-env/bin/activate
    ```
3. Install dependencies: opencv-python should already be there. For YOLO:
    ```bash
    pip3 install ultralytics
    ```

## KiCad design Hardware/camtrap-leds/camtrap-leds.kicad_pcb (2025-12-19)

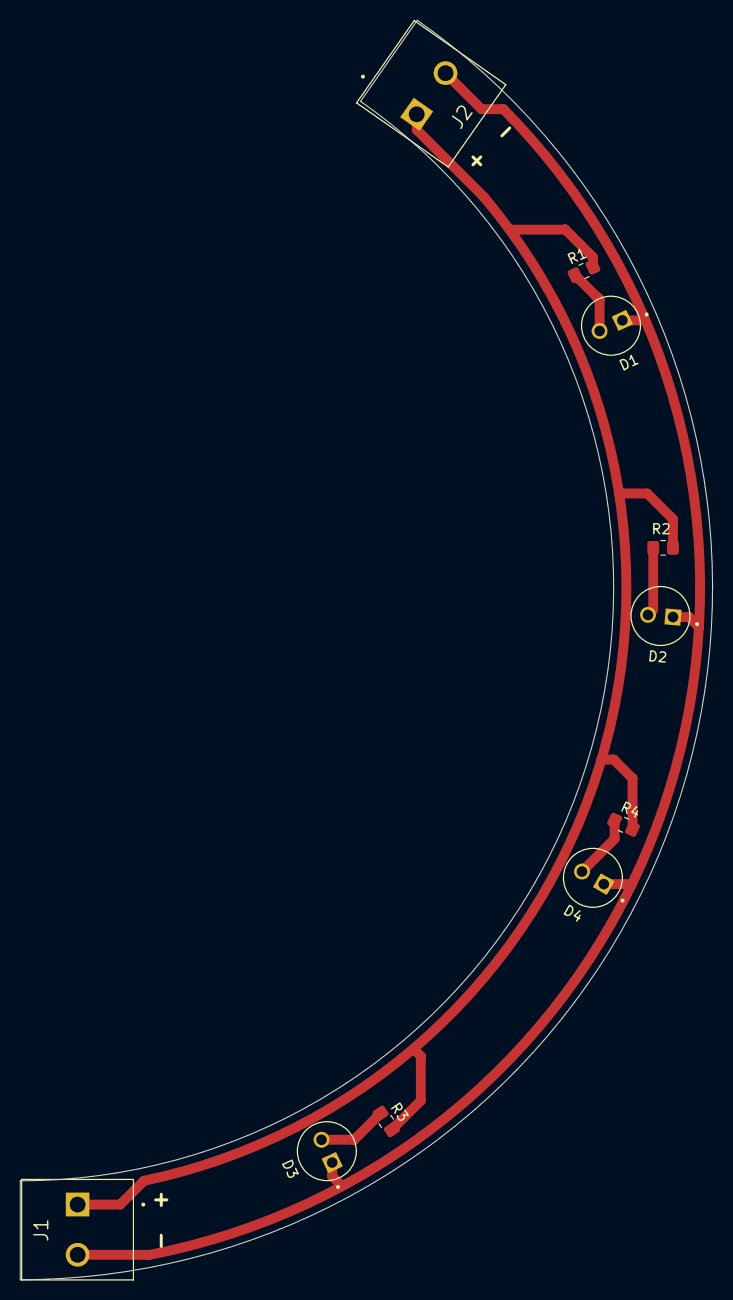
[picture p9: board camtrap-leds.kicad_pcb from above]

Board: 2 copper layers, 70.0 x 127.3 mm, 10 parts (0 on the bottom side), 6 nets.

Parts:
D1, D2, D3, D4: TSHG6400; LEDRD254W55D595H900
J1, J2: TB010-508-02BE; CUI_TB010-508-02BE
R1, R2, R3, R4: R; R_0805_2012Metric_Pad1.20x1.40mm_HandSolder

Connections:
GND: D1.C, D2.C, D3.C, D4.C, J1.2, J2.2
unnamed: D1.A, R1.1
unnamed: D2.A, R2.1
unnamed: D3.A, R3.1
unnamed: D4.A, R4.1
unnamed: J1.1, J2.1, R1.2, R2.2, R3.2, R4.2

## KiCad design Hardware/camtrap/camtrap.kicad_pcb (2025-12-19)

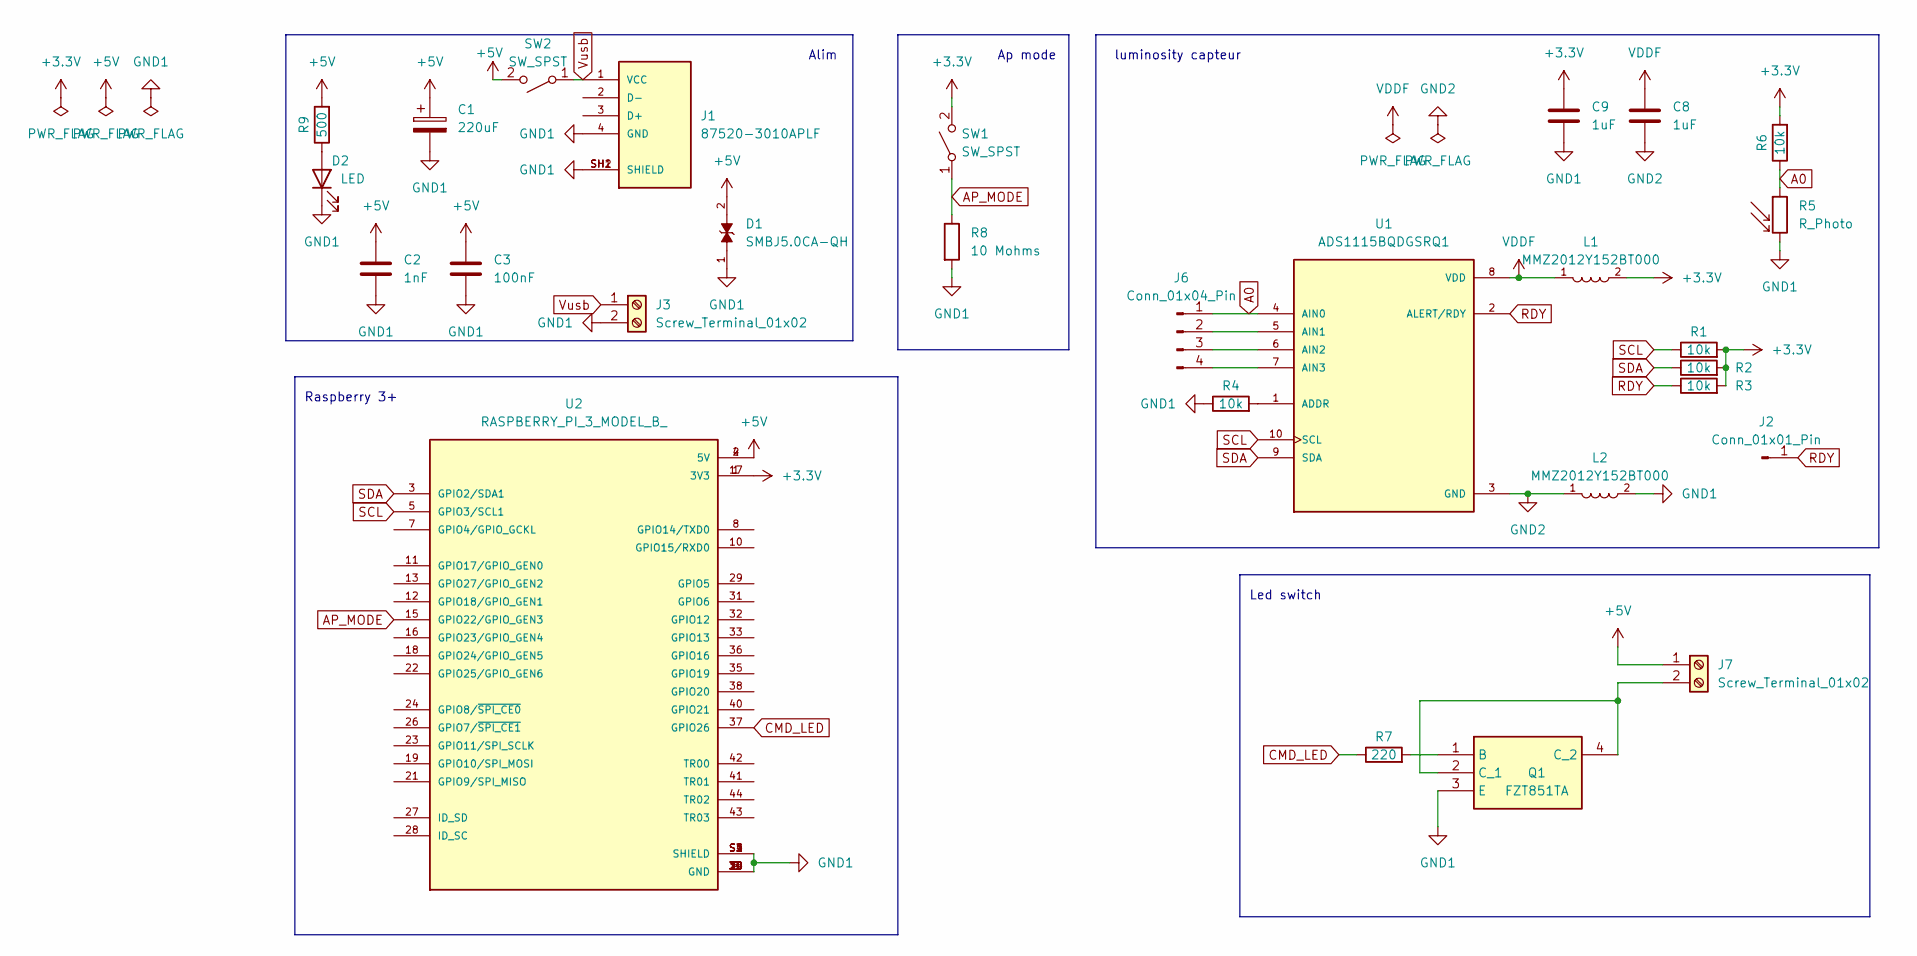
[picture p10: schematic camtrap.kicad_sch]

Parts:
C1: 220uF; CP_Radial_D8.0mm_P3.50mm
C2: 1nF; C_0805_2012Metric_Pad1.18x1.45mm_HandSolder
C3: 100nF; C_0805_2012Metric_Pad1.18x1.45mm_HandSolder
C8, C9: 1uF; C_0805_2012Metric_Pad1.18x1.45mm_HandSolder
D1: SMBJ5.0CA-QH; DIOM4336X265N; PARTREV I2102
D2: LED; PinHeader_1x02_P2.54mm_Vertical
J1: 87520-3010APLF; AMPHENOL_87520-3010APLF; PARTREV AR
J2: Conn_01x01_Pin; PinHeader_1x01_P2.54mm_Vertical
J3, J7: Screw_Terminal_01x02; bornierVis
J6: Conn_01x04_Pin; PinHeader_1x04_P2.54mm_Vertical
L1, L2: MMZ2012Y152BT000; INDC2012X87N
Q1: FZT851TA; SOT230P700X170-4N; Mouser Part Number 522-FZT851TA
R1, R2, R3, R4, R6: 10k; R_0805_2012Metric_Pad1.20x1.40mm_HandSolder
R5: R_Photo; PinHeader_1x02_P2.54mm_Vertical
R7: 220; R_0805_2012Metric_Pad1.20x1.40mm_HandSolder
R8: 10 Mohms; R_0805_2012Metric_Pad1.20x1.40mm_HandSolder
R9: 500; R_0805_2012Metric_Pad1.20x1.40mm_HandSolder
SW1, SW2: SW_SPST; PinHeader_1x02_P2.54mm_Vertical
U1: ADS1115BQDGSRQ1; SOP50P490X110-10N; PARTREV D
U2: RASPBERRY_PI_3_MODEL_B_; raspberrypi 3b+; PARTREV N/A

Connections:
+3.3V: C9.1, L1.2, R1.2, R2.2, R3.2, R6.2, SW1.2 (B), U2.1 (3V3), U2.17 (3V3)
+5V: C1.1, C2.1, C3.1, D1.2, J7.1, R9.2, SW2.2 (B), U2.2 (5V), U2.4 (5V)
A0: J6.1, R5.1, R6.1, U1.4 (AIN0)
AP_MODE: R8.1, SW1.1 (A), U2.15 (GPIO22/GPIO_GEN3)
CMD_LED: R7.1, U2.37 (GPIO26)
GND1: C1.2, C2.2, C3.2, C9.2, D1.1, D2.1 (K), J1.4 (GND), J1.SH1 (SHIELD), J1.SH2 (SHIELD), J3.2, L2.2, Q1.3 (E), R4.1, R5.2, R8.2, U2.6 (GND), U2.9 (GND), U2.14 (GND), U2.20 (GND), U2.25 (GND), U2.30 (GND), U2.34 (GND), U2.39 (GND), U2.S1 (SHIELD), U2.S2 (SHIELD), U2.S3 (SHIELD), U2.S4 (SHIELD)
GND2: C8.2, L2.1, U1.3 (GND)
unnamed: D2.2 (A), R9.1
unnamed: J6.2, U1.5 (AIN1)
unnamed: J6.3, U1.6 (AIN2)
unnamed: J6.4, U1.7 (AIN3)
unnamed: J7.2, Q1.2 (C_1), Q1.4 (C_2)
unnamed: Q1.1 (B), R7.2
unnamed: R4.2, U1.1 (ADDR)
RDY: J2.1, R3.1, U1.2 (ALERT/RDY)
SCL: R1.1, U1.10 (SCL), U2.5 (GPIO3/SCL1)
SDA: R2.1, U1.9 (SDA), U2.3 (GPIO2/SDA1)
VDDF: C8.1, L1.1, U1.8 (VDD)
Vusb: J1.1 (VCC), J3.1, SW2.1 (A)

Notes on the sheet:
Ap mode
luminosity capteur
Raspberry 3+
Led switch
Alim

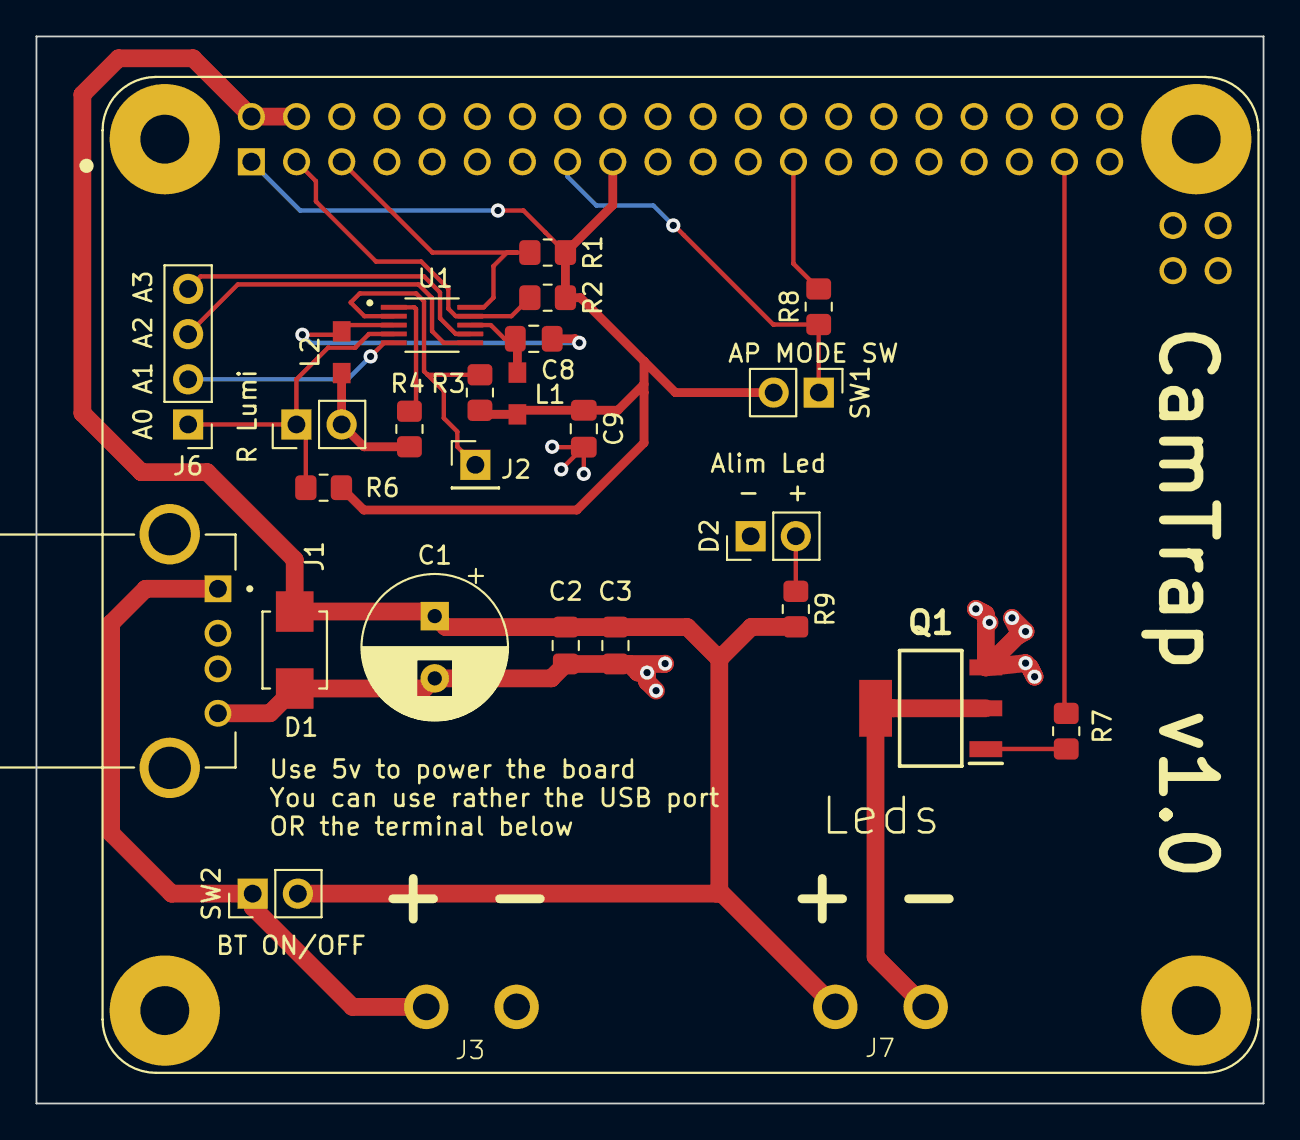
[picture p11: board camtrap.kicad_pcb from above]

Board: 2 copper layers, 69.0 x 60.0 mm, 28 parts (0 on the bottom side), 19 nets.
